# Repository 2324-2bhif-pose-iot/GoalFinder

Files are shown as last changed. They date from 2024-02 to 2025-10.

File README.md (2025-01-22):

# Goal Finder

IoT project in scope of POSE-PRPR and WLC, HTL Leonding, 2BHIF, JG 2324 in cooperation with Universität Wien.

[Erste Schritte](docs/gettting_started_de.md)

## Introduction

When visually impaired people play basket ball, they need acoustic assistance for locating the basket and as feedback if the basket is hit.

For locating the basket, a constant beeping is sufficient. For a hit, a triumph fanfare may be played. Miss detection may result in an according tune.

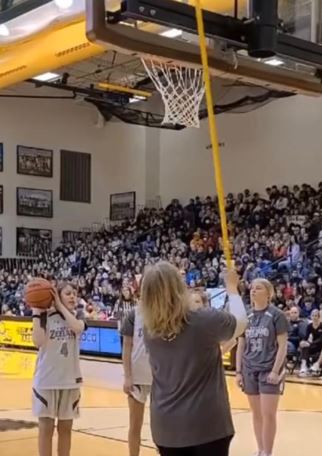
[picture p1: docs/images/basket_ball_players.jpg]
Basketball


Such assistance device may be directly mounted on the basket rack. They shall be easily mountable, e.g. by sliding them on the board or basket.

For hit detection, a short range laser distance sensor (ToF - time of flight sensor) is used. It is looking through the mesh of the basket and is therefore capable detecting a ball falling through the basket.

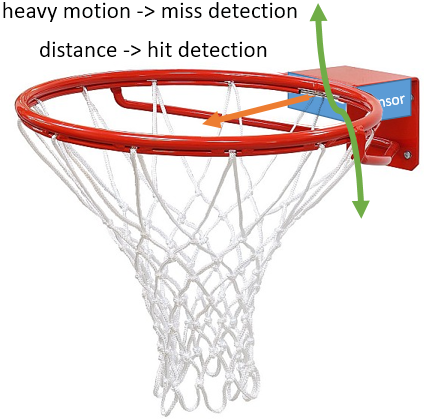
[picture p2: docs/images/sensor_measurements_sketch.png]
Sensor Sketch


Optionally, hitting the basket-board may be detected using an acceleration sensor. When a ball hits the board or the ring, heavy motion can be expected and detected. If the ball does not pass the basket in time, a miss is detected.

The sensor device shall be controlled via a web application designed for mobile devices, to operate the system on the (basketball) field. The application may also assist in the game, for instance by automatically counting hits for multiple players.

## Project Goals

A basketball assistance device as described about shall be developed and deployed in the field.

## Hardware Platform

+ SoC: ESP32, see [Random Nerd Tutorials: ESP32- Pinout](https://randomnerdtutorials.com/esp32-pinout-reference-gpios/)
+ Distance Sensor: ToF sensor connected via I²C, such as VL53L0X. see [YouTube: ToF used with ESP32](https://www.youtube.com/watch?v=HeMlcCDYCEk).
+ Option: Acceleration sensor (TBD).
+ Audio: ESP32 DAC with external pre-amplifier, see [YouTube: ESP32 Audio: I2S & Built-In DACs Explained](https://www.youtube.com/watch?v=lgDu88Y411o)
+ Power supply: Grid via power adapter or power bank.

## Use Cases and User Stories

1. As a user, I want to control the device via web application on a smart phone as well as on a desktop PC.
1. As a player, I want the device to provide acoustic hints of the basket location.
1. As a player, I want the device to sound a triumph tune when the ball hits the basket.
1. As a player, it would be great to hear a sound when the ball hits the basket rack but not the basket.
1. As a user, I want to connect to the device via WiFi network that is spread by the device.
1. As a user, I want to integrate the device into my WiFi network easily.
1. As a user, I want that the device time is synchronized with the real time of my timezone.
1. As a user, I want to update the device software over the air.

## Tasks

This section describes the first task to be tackled on a high-level base.

1. Specify a roadmap / time table for the given tasks and user story implementation.
1. Develop a software design showing the major software components and their relations as well as required communication protocols.
1. Integrate a WiFi setup and configuration on the device.
1. Integrate a web server on the device.
1. Integrate an SNTP client on the device, including SNTP configuration via integrated web server.
1. Implement the SW-component to measure distances via distance senor.
1. Option: Implement SW-component to measure motion via motion sensor.
1. Implement hit / miss detection based on the measured values.
1. Implement audio output
1. Integrate suitable audio tracks for signalling events.
1. Option: Implement audio feedback via Bluetooth.
1. Implement a web front-end suitable for configuring the sensor device
1. Implement a web front-end for game play.
1. Integrate and enable SWUOTA (software update over the air).

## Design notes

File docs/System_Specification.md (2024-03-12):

# System Specification

Hardware: 
- ESP32
- Distance Sensor
- Optional: Acceleration Sensor
- Audio ESP32
- Power Supply (power bank or power adapter)
  
Software:
- WiFi Client and WLAN integration
- Web Server
- SNTP Client
- Distance Sensor Software
- Optional: Motion Sensor Software
- Hit / Miss Detection
- Audio output, tracks, feedback (Audio manager)
- Web Application
- SWUOTA

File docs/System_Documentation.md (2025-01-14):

# Goalfinder System Documentation

## Summary

The Goalfinder is a device for visually impaired people, that need assistence locating the basket when playing basketball. This is done by a constant sound being played so that they can locate the basket. When a goal is scored a user specificated fanfare is played.

## Pin Configuration

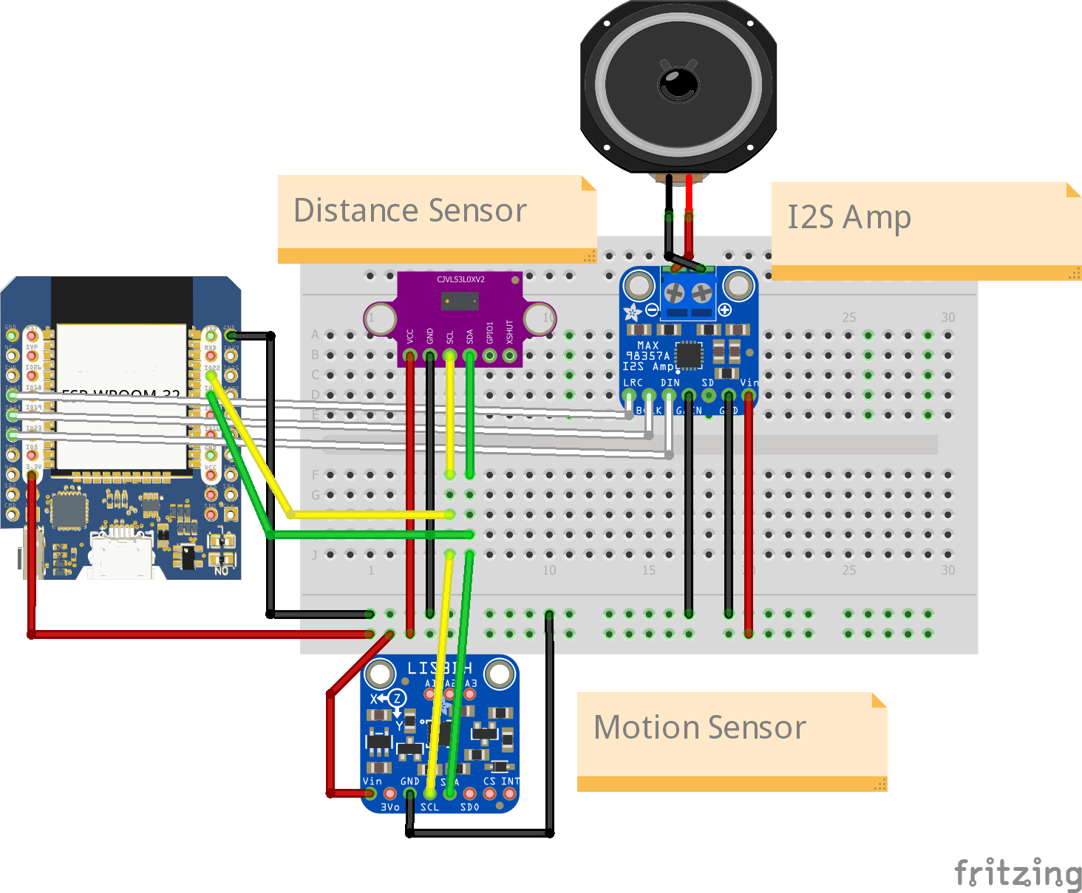
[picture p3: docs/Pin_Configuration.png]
Pins


### Components

- Distance Sensor
- Motion Sensor
- I2S Amp
- ESP 32

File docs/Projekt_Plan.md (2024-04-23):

# Projektplan

## Mitglieder
- Alex (A)
- Omar (O)
- Edin (E)
- Rabbi (R)

## Aufteilung
| Projektteil | Wer | Beginn    |
|-------------|-----|-------------|
| WLAN (HW)   | Alex |
| Web App | Alle |
| Web Server / SNTP Client (HW) | Alex / Omar
| Audio | Alex, Edin |
| Bluetooth Audio | Rabbi |
| ToF Sensor | Omar |
| Vibration Sensor | Rabbi |
| SWUOTA | Edin
| Optionale Sachen und Optimierung | Alle | Ende |

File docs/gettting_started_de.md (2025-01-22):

# Erste Schritte - Anleitung

## Inhaltsverzeichnis
- [Manuelles Flashen](#manuelles-flashen)
   - [Voraussetzungen (Tools)](#voraussetzungen-tools)
   - [Flashen des Systems](#flashen-des-systems)

- [Update über Webapp](#update-über-webapp)

Wenn der GoalFinder noch nicht aufgesetzt wurde oder der Flash-Speicher zurückgesetzt wurde, muss man die Firmware und das Filesystem manuell auf den GoalFinder flashen. Ansonsten kann man die neuste Firmware und das neuste Filesystem auf den GoalFinder über die Webapp laden.

## Manuelles Flashen

### Voraussetzungen (Tools)
- [CP210x Universal Windows Driver](https://www.silabs.com/developer-tools/usb-to-uart-bridge-vcp-drivers?tab=downloads)
- [Python](https://www.python.org/downloads/)

#### Installieren des Treibers
1. Entpacken Sie die Datei `CP210x_Universal_Windows_Driver.zip`
2. Öffnen Sie den entpackten Ordner
3. Drücken Sie mit der rechten Maustaste auf die Datei `silabser.inf` und wählen Sie `Installieren` aus
4. Folgen Sie den Anweisungen auf dem Bildschirm
5. Nun ist der erforderliche Treiber installiert

#### Installieren von Python und esptool.py
1. Installieren Sie die neuste Version von [Python](https://www.python.org/downloads/)
2. Führen Sie den Installer aus und folgen Sie den Anweisungen auf dem Bildschirm
3. Nun sollte Python installiert sein
4. Öffnen Sie die Eingabeaufforderung und führen Sie folgenden Befehl aus um `esptool.py` zu installieren.
   ``` 
   pip install esptool
   ```

### Flashen des Systems
1. Bauen Sie den GoalFinder auseinander um zum Micro-USB des ESP32 zu gelangen
2. Verbinden Sie den GoalFinder mithilfe eines Micro-USB Kabels mit dem Computer
3. Laden Sie die neusten `system.bin` und `littlefs.bin` Dateien von [Releases](https://github.com/2324-2bhif-pose-iot/GoalFinder/releases/latest) runter
4. Öffnen Sie die Eingabeaufforderung und navigieren Sie zum Ordner mit den heruntergeladenen Dateien mithilfe von dem Befehl `cd C:\Pfad\zum\Ordner`
5. Führen Sie folgenden Befehl in der Eingabeaufforderung aus um die Firmware zu flashen:
   ```
   python -m esptool -b 921600 write_flash 0x0 system.bin
   ```
6. Führen Sie folgenden Befehl in der Eingabeaufforderung aus um das Filesystem zu flashen:
   ```
   python -m esptool -b 921600 write_flash 2686976 littlefs.bin
   ```
7. Nun ist der GoalFinder betriebsbereit. Nun kann der GoalFinder durch die Webapp aktualisiert werden.

## Update über Webapp
1. Laden Sie die neusten `firmware.bin` und `littlefs.bin` Dateien von [Releases](https://github.com/2324-2bhif-pose-iot/GoalFinder/releases/latest) runter
2. Schließen Sie den GoalFinder an eine Stromquelle an
3. Verbinden Sie sich mit dem WiFi-Netz des GoalFinders
4. Öffnen Sie ihren Browser und geben Sie in die Adressleiste `goalfinder.local` ein
5. Es sollte sich nun die Webapp des GoalFinders öffnen
6. Navigieren Sie zu `Einstellungen > System`
7. Unter dem Punkt `Software Aktualisierung` drücken Sie auf `Auf Aktualisierung prüfen`
8. Wählen Sie zuerst `Firmware` und wählen Sie die zuvor heruntergeladene Datei `firmware.bin` aus
9. Warten Sie bis der Updatevorgang abgeschlossen wurde
10. Nun wird der Vorgang für das Filesystem wiederholt. Dabei wird `Filesystem` und anschließend die Datei `littlefs.bin` ausgewählt
11. Nun sollte der GoalFinder auf dem neusten Stand sein

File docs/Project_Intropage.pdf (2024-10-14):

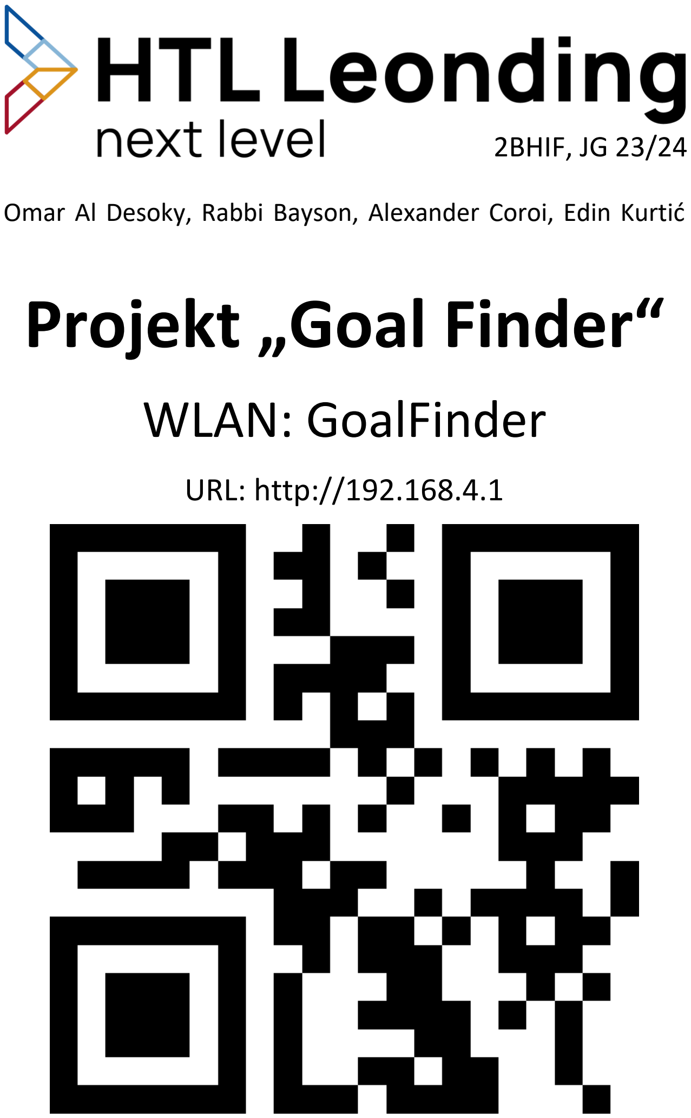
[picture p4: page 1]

Omar Al Desoky, Rabbi Bayson, Alexander Coroi, Edin Kurtić

# Projekt „Goal Finder“

# WLAN: GoalFinder

### URL: http://192.168.4.1

2BHIF, JG 23/24

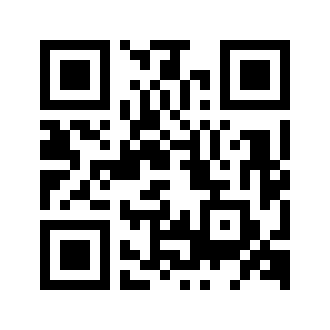
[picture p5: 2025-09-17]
docs/images/wifi_qr_goalfinder.png

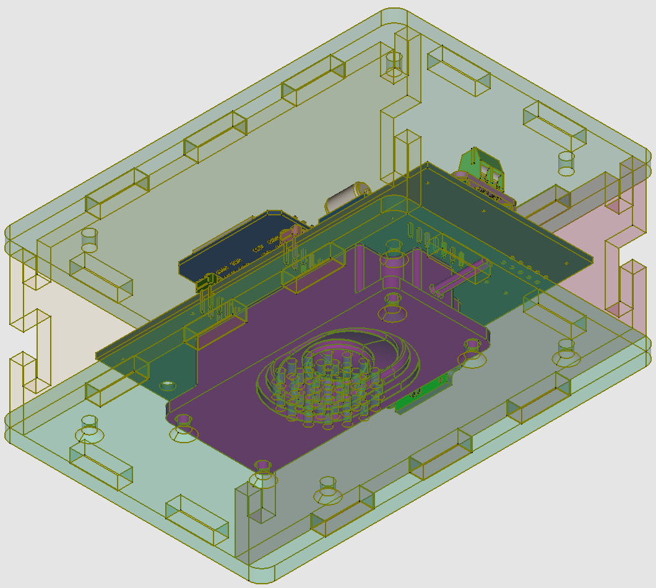
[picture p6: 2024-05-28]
docs/images/Goalfinder_r1.2_Case_r1.0_bottom.png

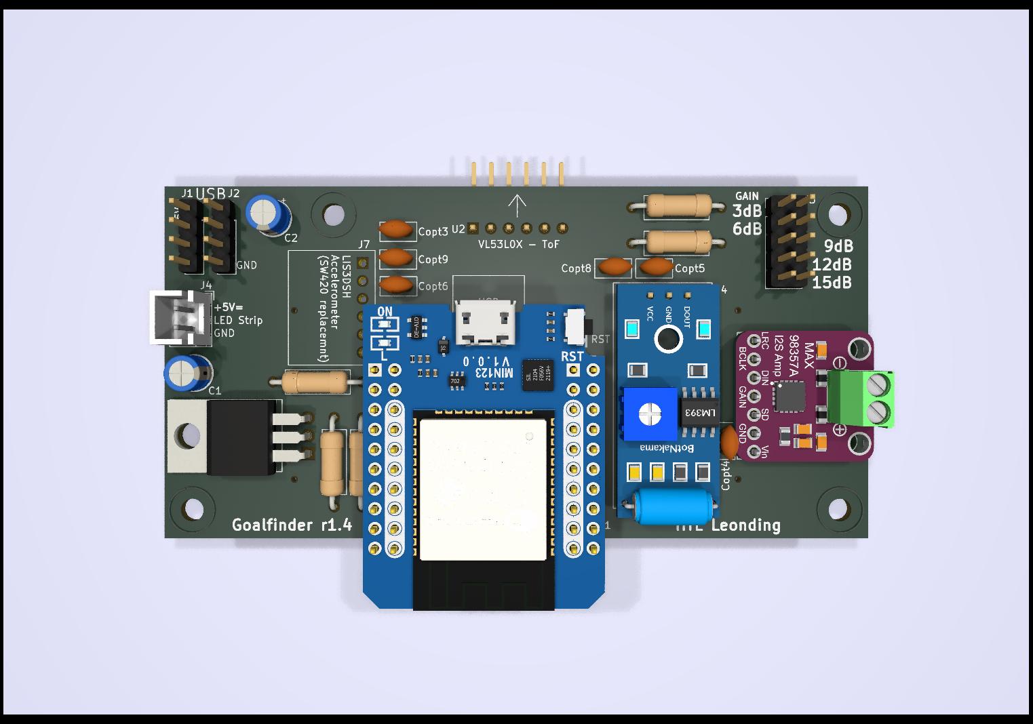
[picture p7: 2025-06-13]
docs/images/Goalfinder_PCB_r1.4_THT_Vibration_front.jpg

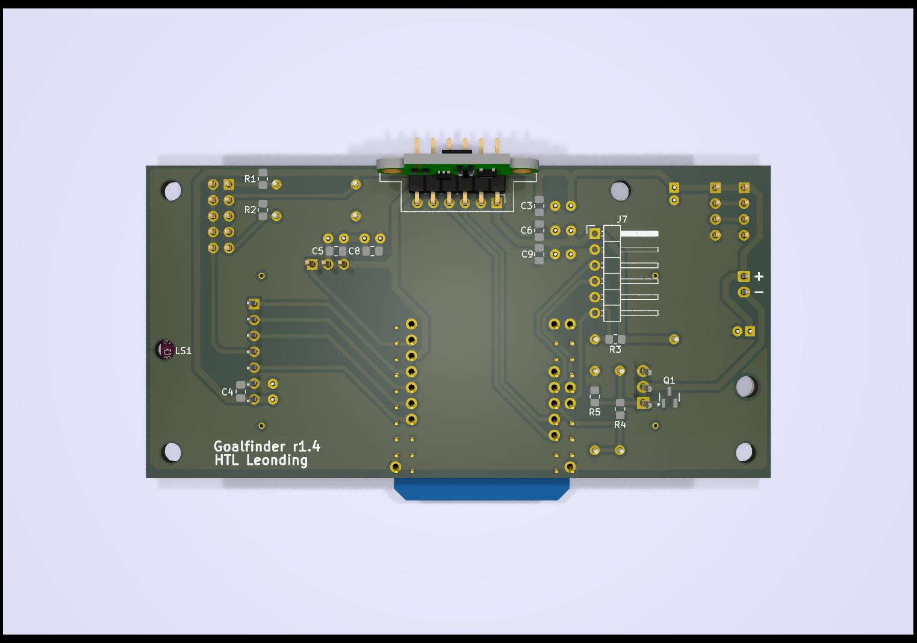
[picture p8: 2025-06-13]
docs/images/Goalfinder_PCB_r1.4_THT_Vibration_back.jpg

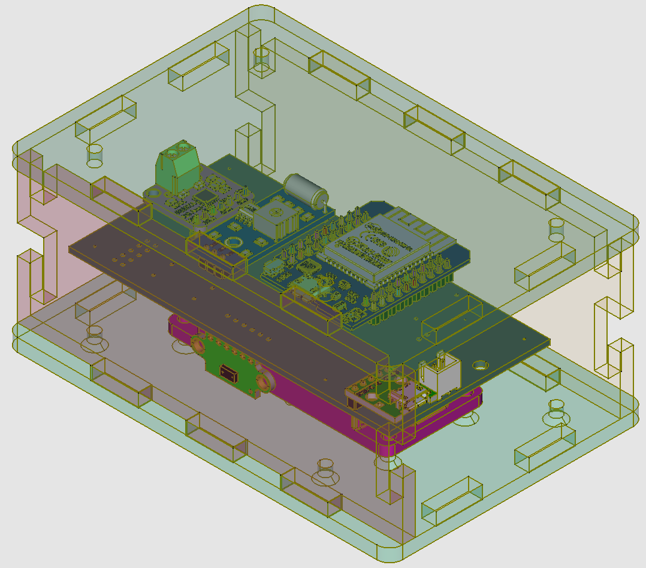
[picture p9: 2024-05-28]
docs/images/Goalfinder_r1.2_Case_r1.0_top.png

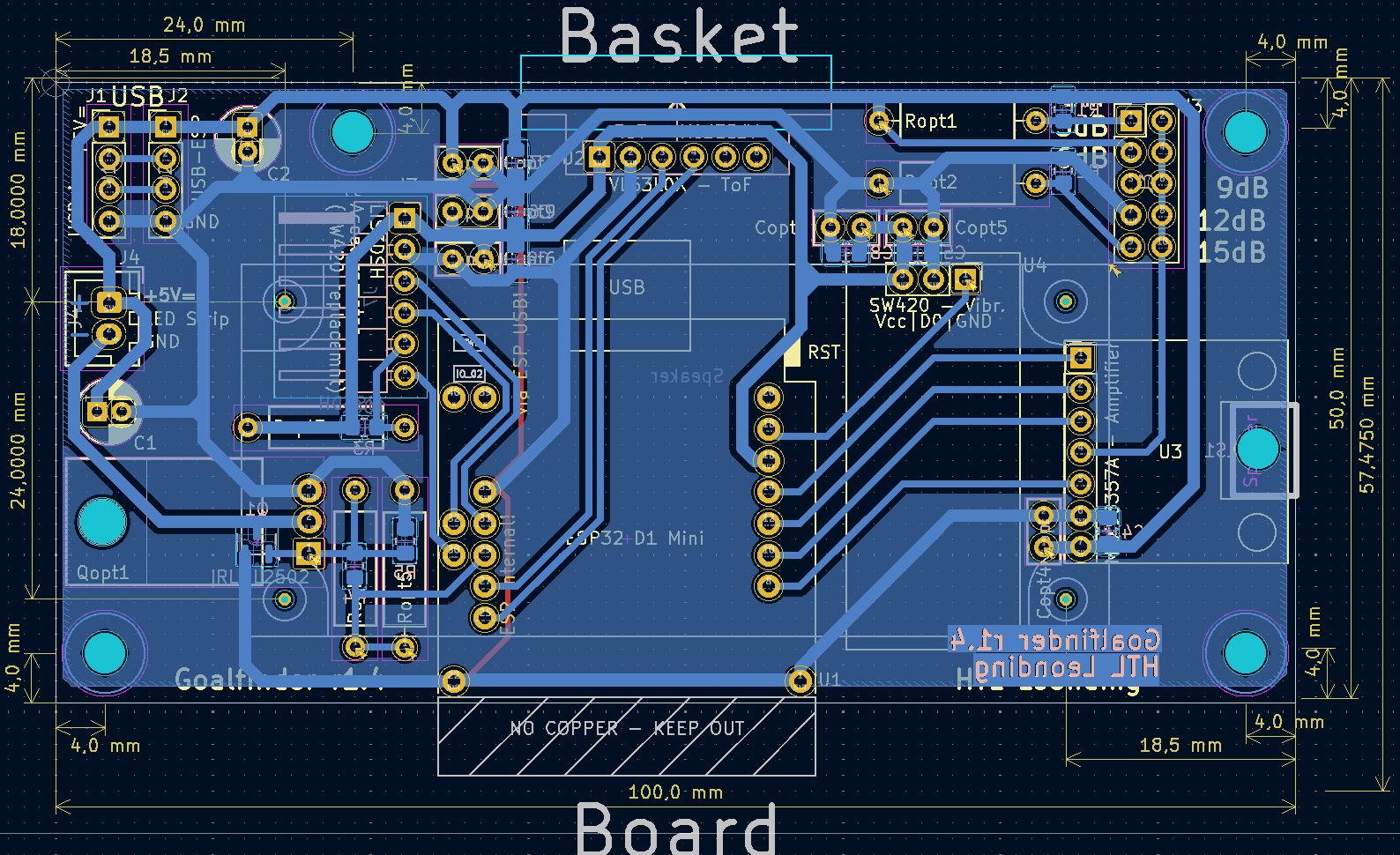
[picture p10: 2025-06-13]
docs/Goalfinder_PCB_r1.4_layout.png

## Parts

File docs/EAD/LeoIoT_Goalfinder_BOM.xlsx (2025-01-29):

Reference | Value | Footprint | Qty | Beschreibung | Comment / Supplier
C1 | 22µF | Capacitor_THT:CP_Radial_D5.0mm_P2.00mm | 1 | Polarized capacitor, small symbol
C2 | 4,7µF | Capacitor_THT:CP_Radial_D5.0mm_P2.00mm | 1 | Unpolarized capacitor, small symbol
C3 | 0,1µF | Capacitor_THT:C_Rect_L13.0mm_W4.0mm_P10.00mm_FKS3_FKP3_MKS4 | 1 | Unpolarized capacitor, small symbol
C4,C5,C6,C7,C8 | 100nF | Capacitor_SMD:C_0805_2012Metric_Pad1.18x1.45mm_HandSolder | 5 | Unpolarized capacitor, small symbol
Copt4,Copt5,Copt6,Copt7,Copt8 | 100nF | Capacitor_THT:C_Disc_D5.0mm_W2.5mm_P2.50mm | 0 | Unpolarized capacitor, small symbol | Optional for THT parts, replaces C4, C5, C6, C7, C8 https://www.reichelt.de/de/de/shop/produkt/keramik-kondensator_100_nf_-20_80_y5v_50_100_v_rm_5-9265
J2 | LED Strip | Connector_JST_2.54:JST_XH_B2B-XH-A_1x02_P2.54mm_Vertical | 1 | Connector for LED Strip
J1 | USB_B_Micro_Breakout | Breakout_Boards:Micro-USB_BreakoutBoard | 1 | USB Micro Type B connector | https://www.amazon.de/KARELLS-Steckerkabel-Verl%C3%A4ngerungskabel-Stromladekabel-Ersatzkabel/dp/B0D6362W88
D1, J1e1 | Conn_01x02_Pin | 5V LED Strip, max 30W | 1 | LED Strip with connector suitable for J2 | https://www.amazon.de/GOMING-COB-Selbstklebend-Wasserdicht-Lichtband/dp/B09VGR6PWH/ref=sr_1_4?th=1
J3 | GAIN | Connector_PinHeader_2.54mm:PinHeader_2x05_P2.54mm_Vertical | 1 | Jumper bar for gain selection | either wire bridge or:
 |  |  |  |  | Jumper: https://www.reichelt.de/de/de/shop/produkt/kurzschlussbruecke_schw_m_grifflasche-9019
 |  |  |  |  | Pin Header: https://www.reichelt.de/de/de/shop/produkt/stiftleiste_2x20-pol_vergoldet_2_54mm-235664
LS1 | Speaker | Breakout_Boards:Mono-Enclosed_Speaker_70x30x17mm_onboard | 1 | Speaker, 3 W, 8 Ohm | https://www.amazon.de/dp/B09PL6XFHC
Q1 | IRFZ44N | Package_TO_SOT_THT:TO-220-3_Horizontal_TabDown | 1 | FET | https://www.reichelt.de/de/de/shop/produkt/mosfet_n-ch_60v_48a_110w_0_023r_to220ab-257487
R1,R2 | 100k | Resistor_THT:R_Axial_DIN0309_L9.0mm_D3.2mm_P12.70mm_Horizontal | 2 | Resistor
R4 | 1k | Resistor_THT:R_Axial_DIN0309_L9.0mm_D3.2mm_P12.70mm_Horizontal | 1 | Resistor
R5 | 33k | Resistor_THT:R_Axial_DIN0309_L9.0mm_D3.2mm_P12.70mm_Horizontal | 1 | Resistor
U1 | ESP32_D1_mini | ESP32_D1_mini:ESP32_D1_mini | 1 | ESP32 D1 mini from AZ-Delivery | https://www.amazon.de/AZDelivery-Bluetooth-Internet-Entwicklungsboard-kompatibel/dp/B08BTYCGVV
U2 | VL53L0X_Breakout | Breakout_Boards:VL53L0X_Breakout_Board_vertical_flat | 1 | 2m distance ranging ToF sensor, Optical LGA12 | https://www.amazon.de/AZDelivery-VL53L0X-Flight-kompatibel-Arduino/dp/B086TSNTFD
U3 | MAX98357A_Breakout | Breakout_Boards:MAX98357A_Breakout_Board | 1 | Mono DAC with amplifier, I2S, PCM, TDM, 32-bit, 96khz, 3.2W, TQFP-16 | https://www.amazon.de/AZDelivery-filterloses-Breakout-Modul-Decoder-Modul-Anwendungsbereich/dp/B09PL947ZG
U4 | SW420_Breakout | Breakout_Boards:SW420_Breakout_Board_Horizontal | 1 | Vibrationsensor, Shocksensor | https://www.amazon.de/AZDelivery-Vibration-Sch%C3%BCttel-Ersch%C3%BCtterung-Arduino/dp/B07V9CZ89G

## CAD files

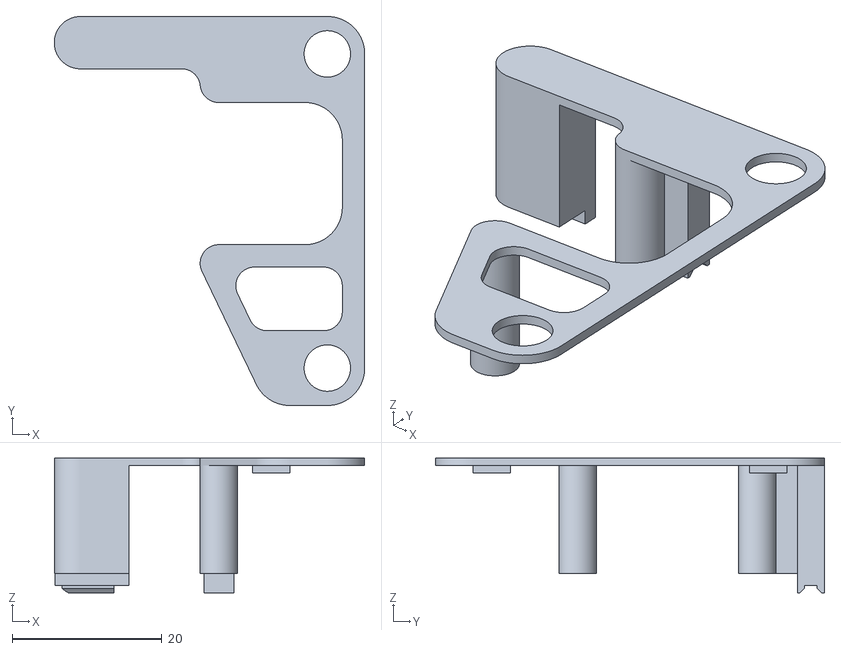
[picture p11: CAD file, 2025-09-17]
docs/Housing/LeoIoT-Goalfinder_r1.4_cpct_Bracket_Top-Right.stl
41.5 x 52.0 x 18.0

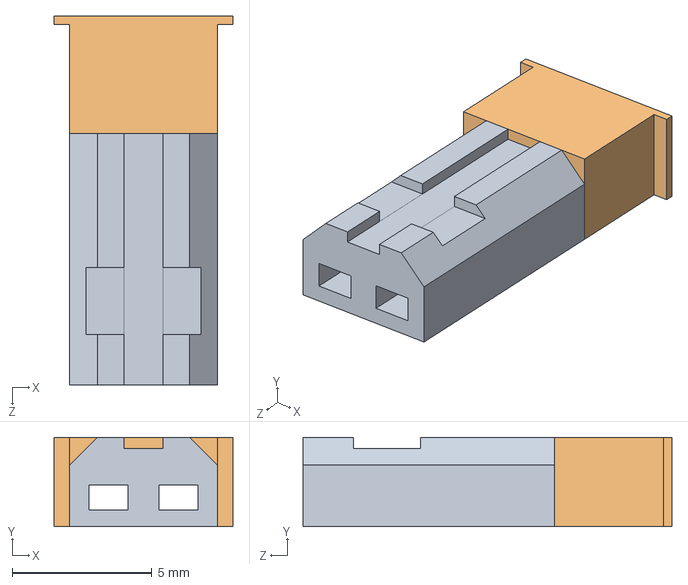
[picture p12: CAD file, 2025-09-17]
docs/Housing/JST-SYP_Female.step
6.40 x 3.20 x 13.2 mm

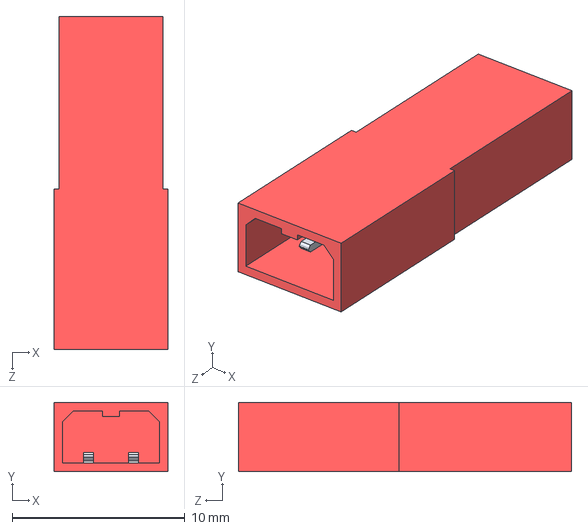
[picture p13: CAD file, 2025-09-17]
docs/Housing/JST-SYP_Male.step
6.60 x 4.00 x 19.3 mm

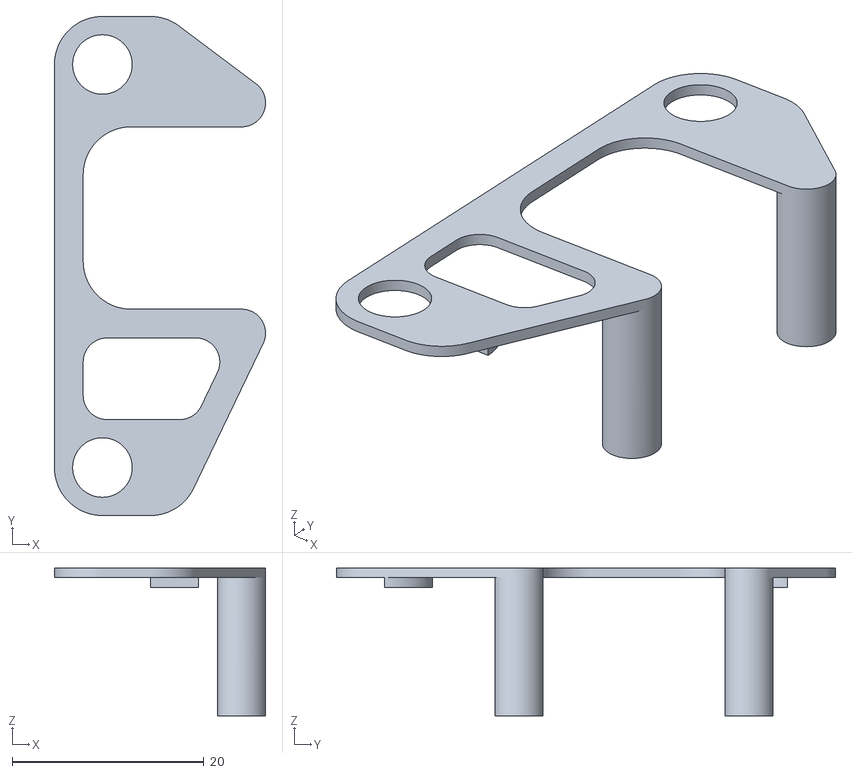
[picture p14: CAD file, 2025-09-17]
docs/Housing/LeoIoT-Goalfinder_r1.4_cpct_Bracket_Top-Left.stl
22.0 x 52.0 x 15.4

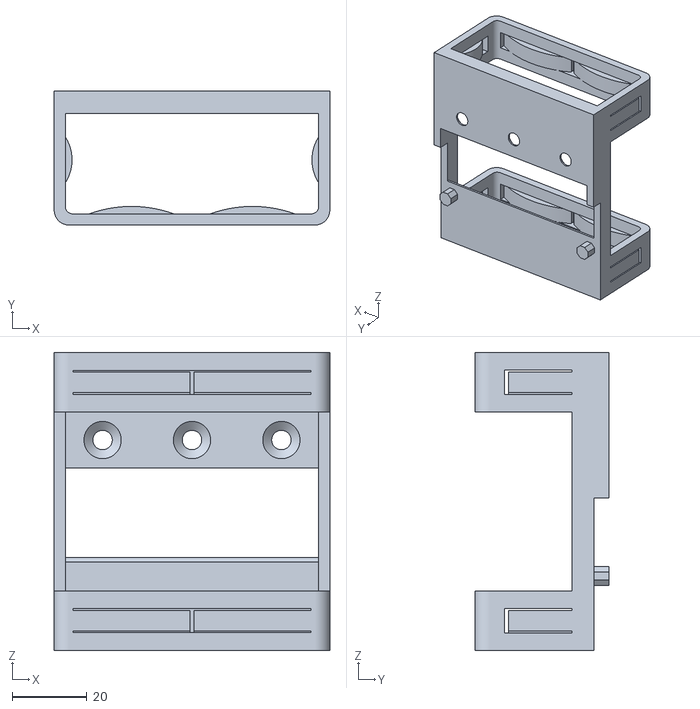
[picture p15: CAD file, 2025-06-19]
docs/Housing/Powerbank-Holder_Anker.stl
74.0 x 36.0 x 80.0

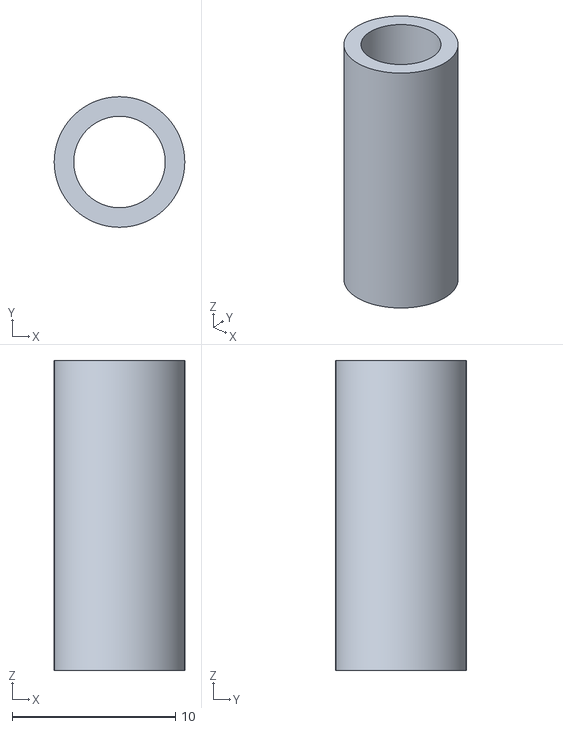
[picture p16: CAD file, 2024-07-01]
docs/Housing/Distance-19.stl
8.00 x 8.00 x 19.0

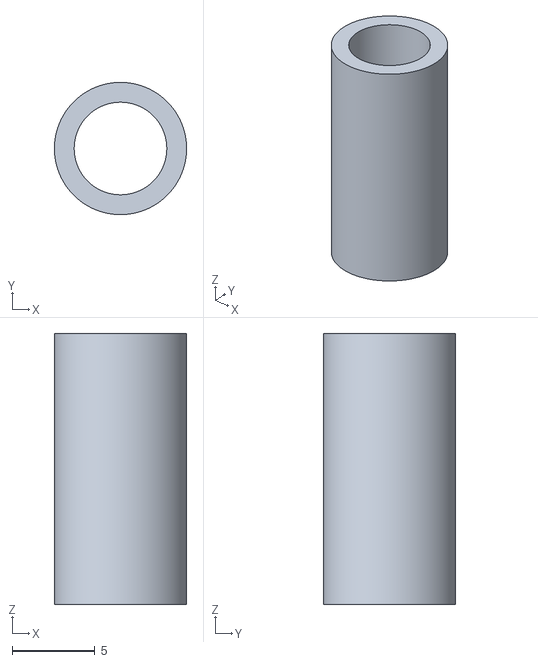
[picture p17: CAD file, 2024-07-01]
docs/Housing/Distance-16.4.stl
8.00 x 8.00 x 16.4

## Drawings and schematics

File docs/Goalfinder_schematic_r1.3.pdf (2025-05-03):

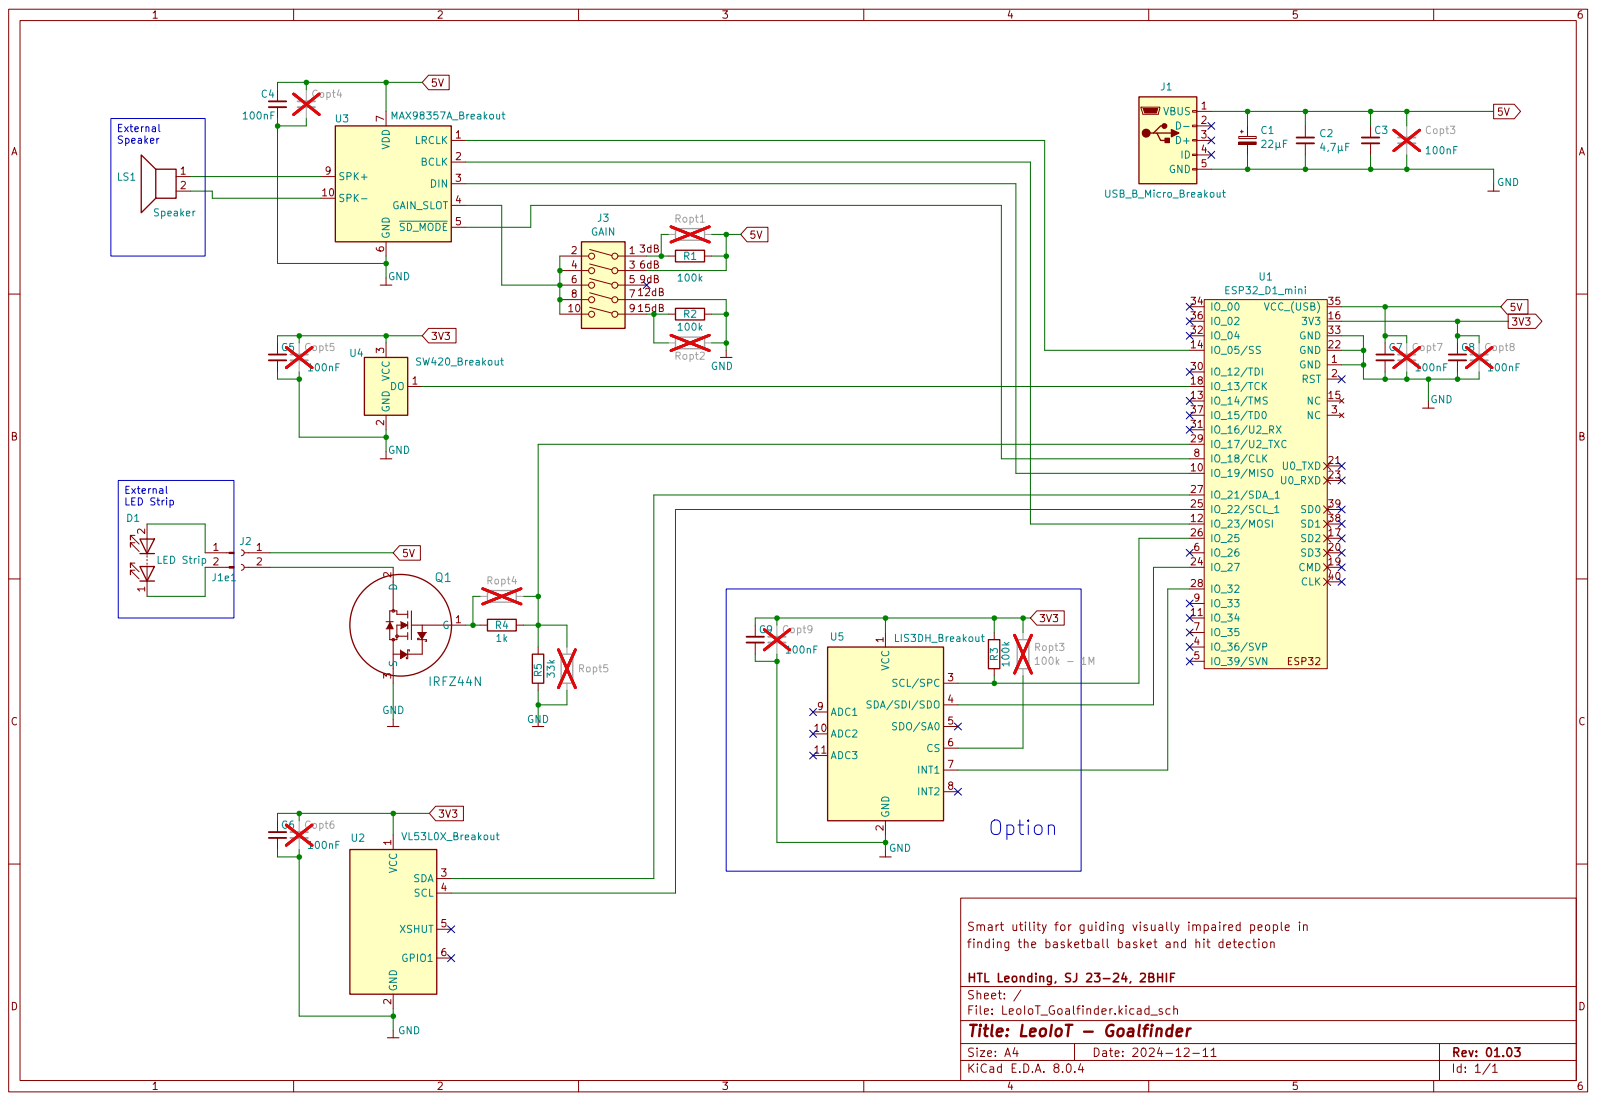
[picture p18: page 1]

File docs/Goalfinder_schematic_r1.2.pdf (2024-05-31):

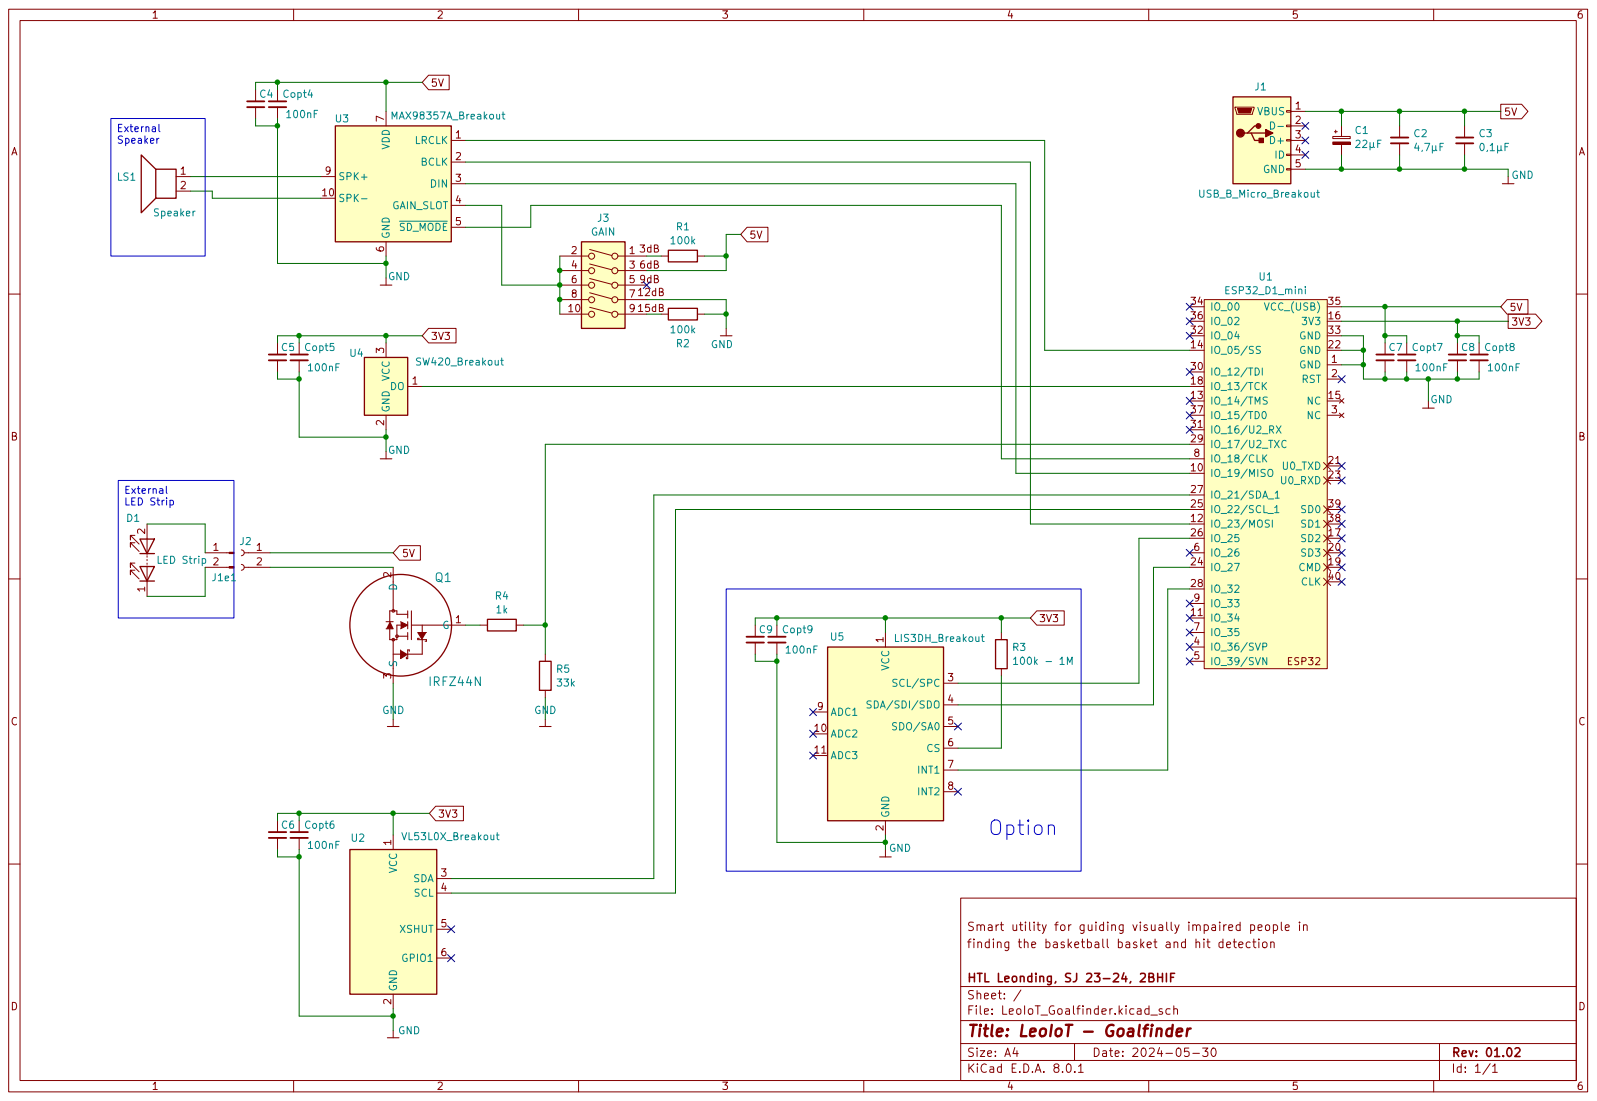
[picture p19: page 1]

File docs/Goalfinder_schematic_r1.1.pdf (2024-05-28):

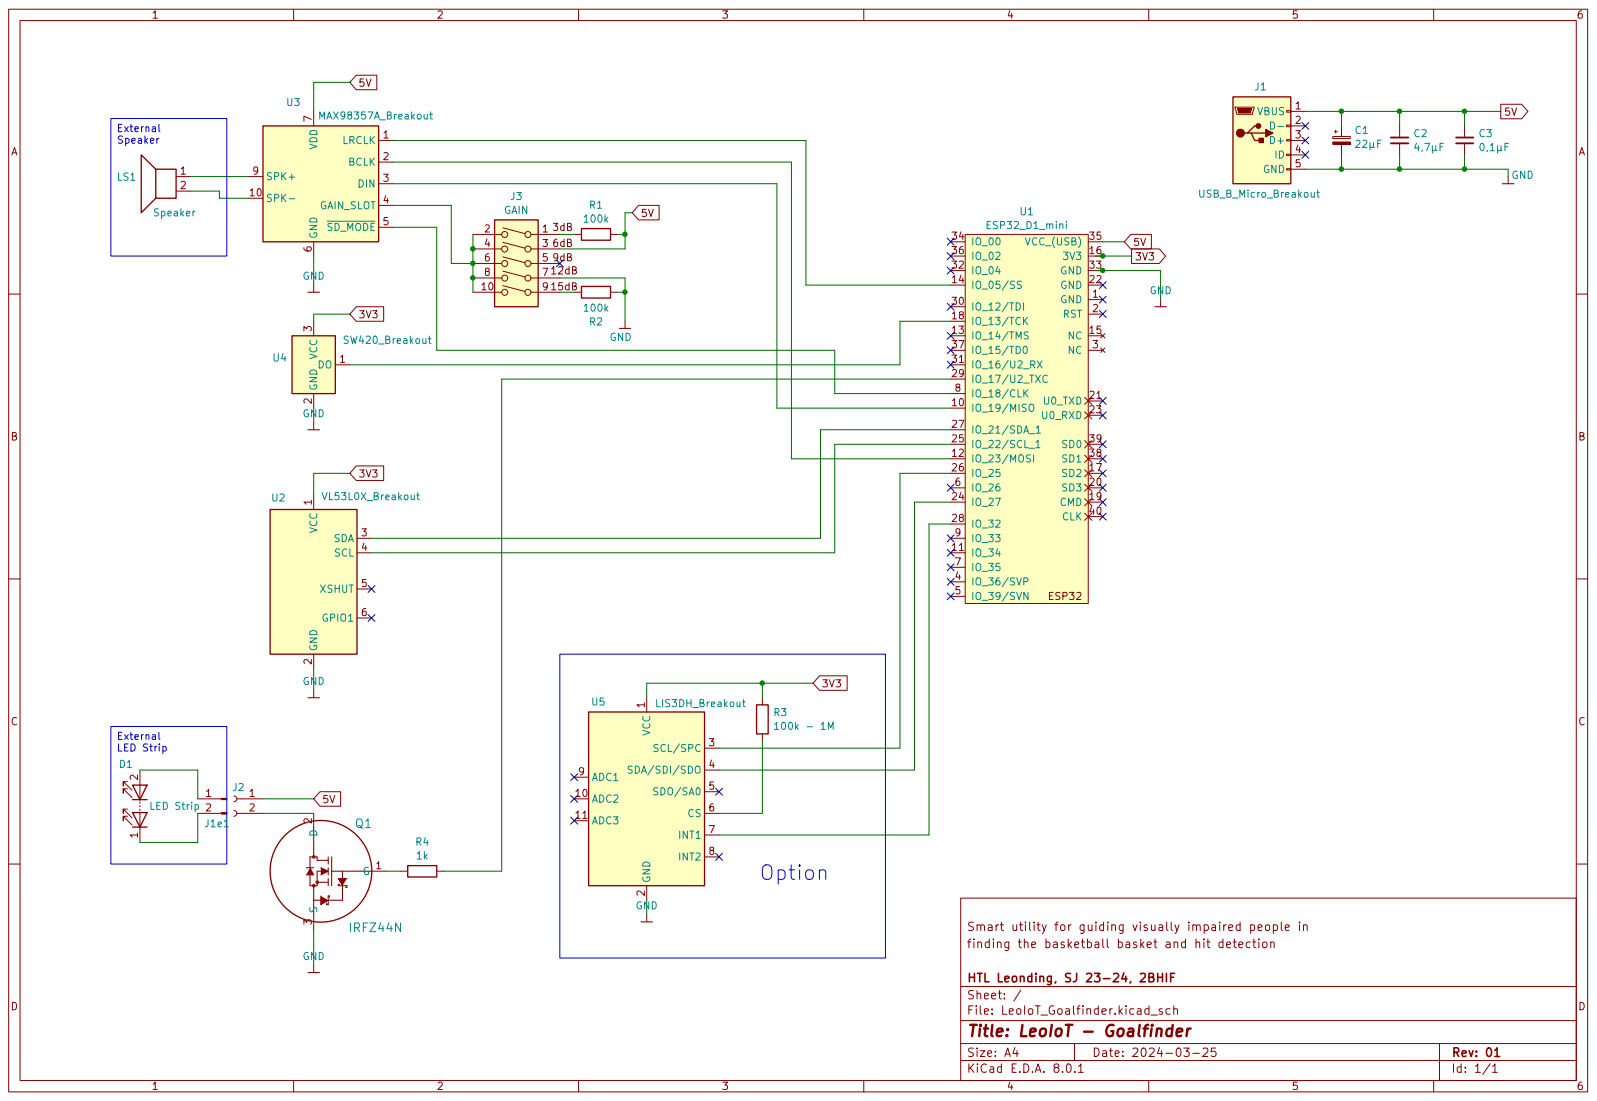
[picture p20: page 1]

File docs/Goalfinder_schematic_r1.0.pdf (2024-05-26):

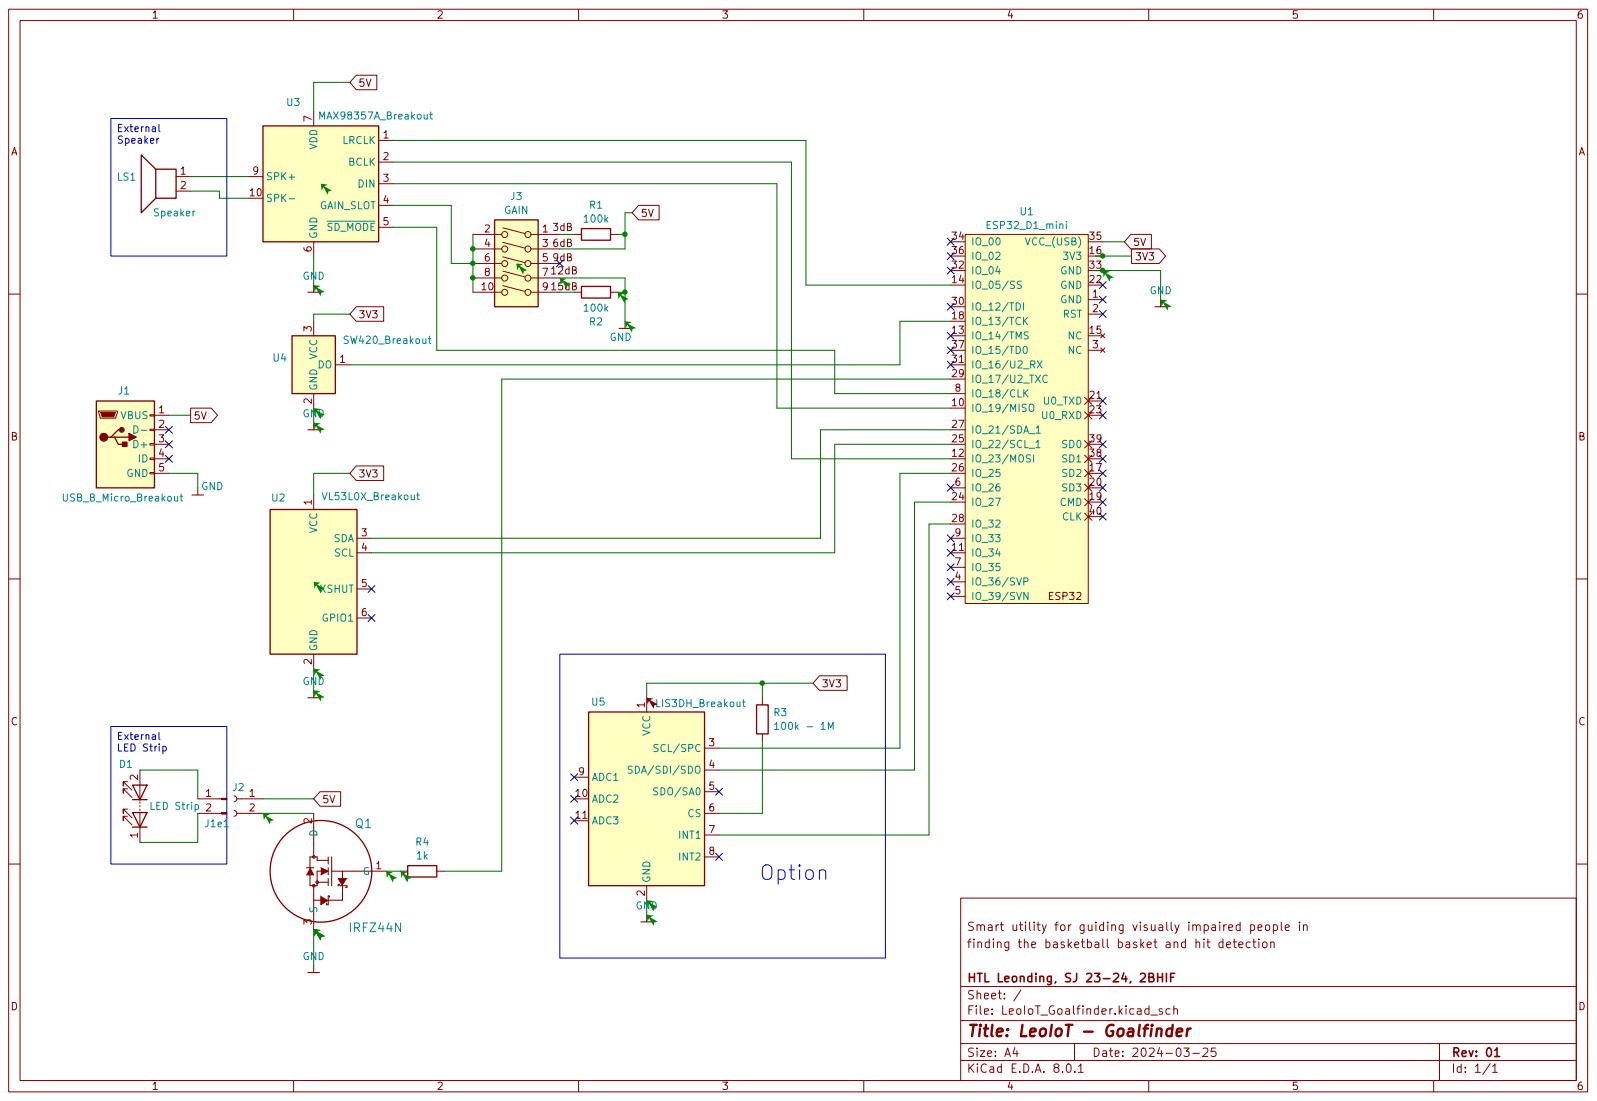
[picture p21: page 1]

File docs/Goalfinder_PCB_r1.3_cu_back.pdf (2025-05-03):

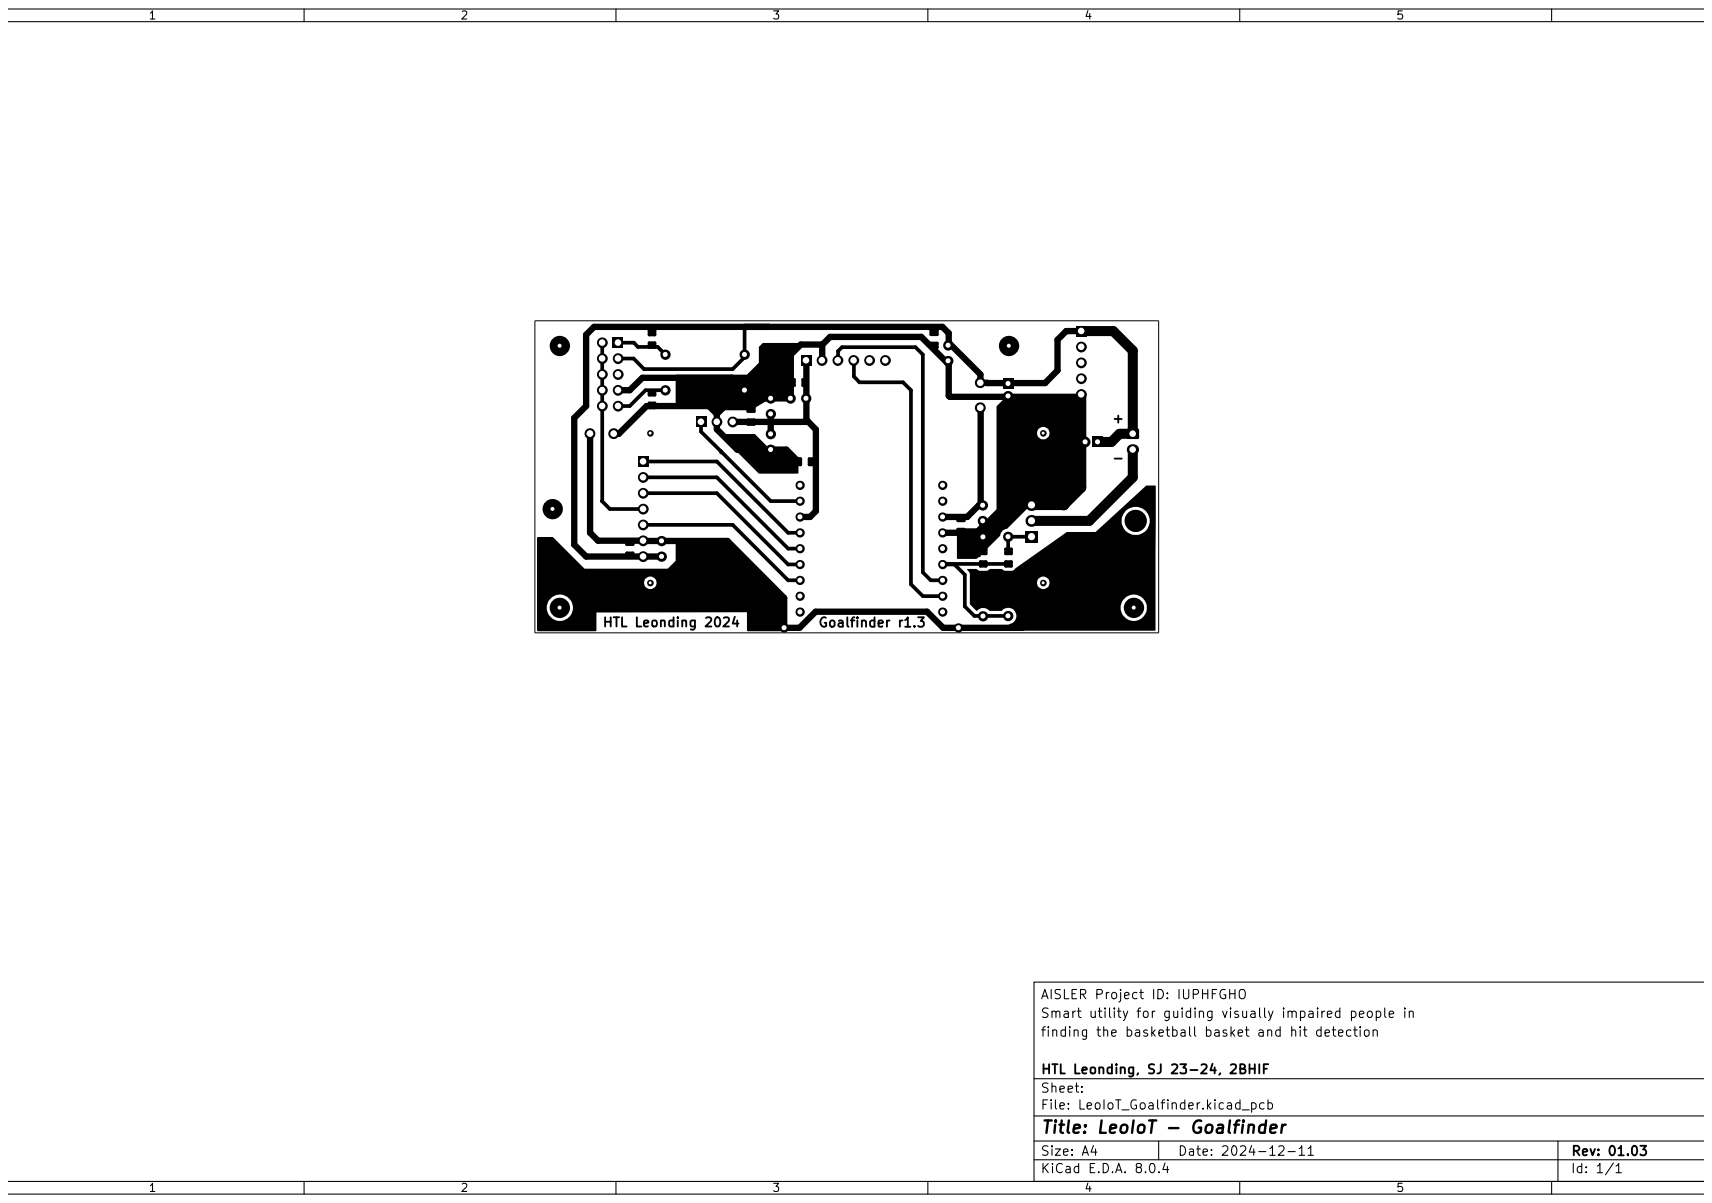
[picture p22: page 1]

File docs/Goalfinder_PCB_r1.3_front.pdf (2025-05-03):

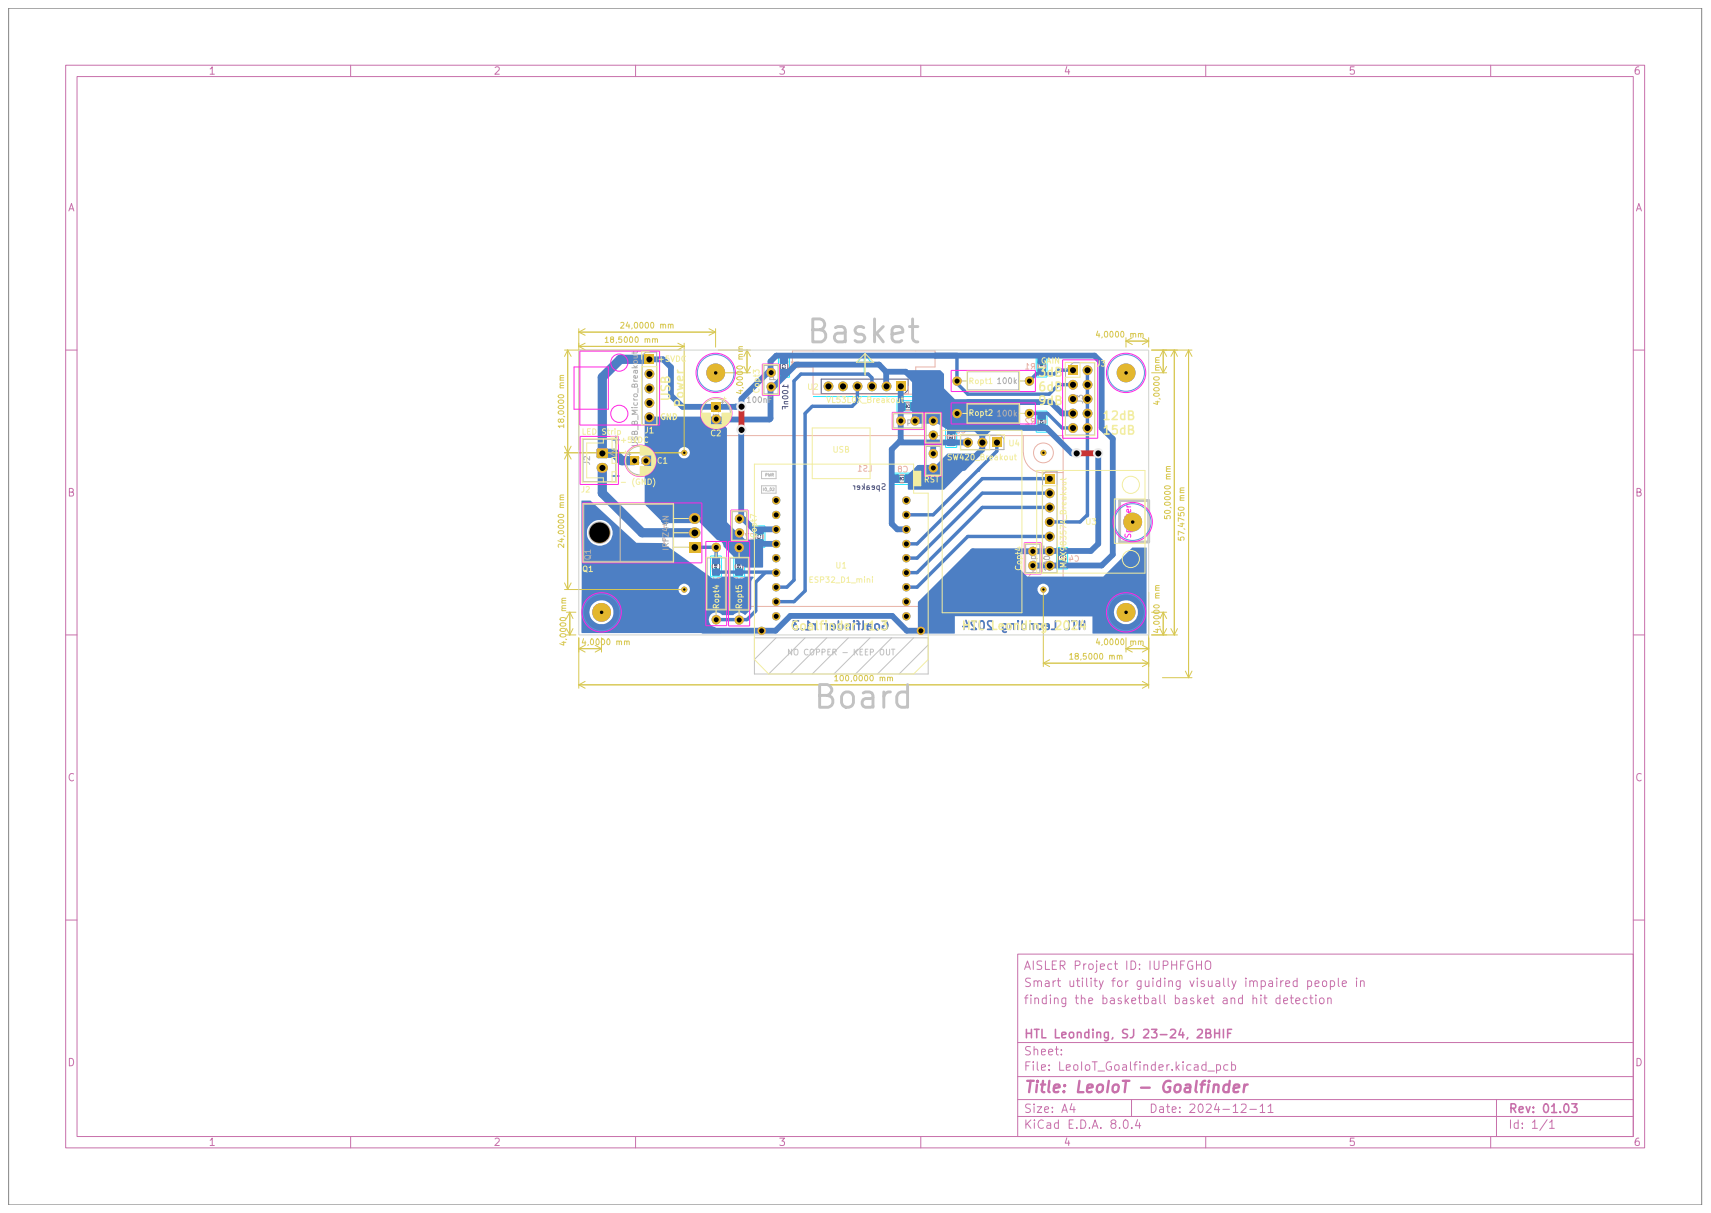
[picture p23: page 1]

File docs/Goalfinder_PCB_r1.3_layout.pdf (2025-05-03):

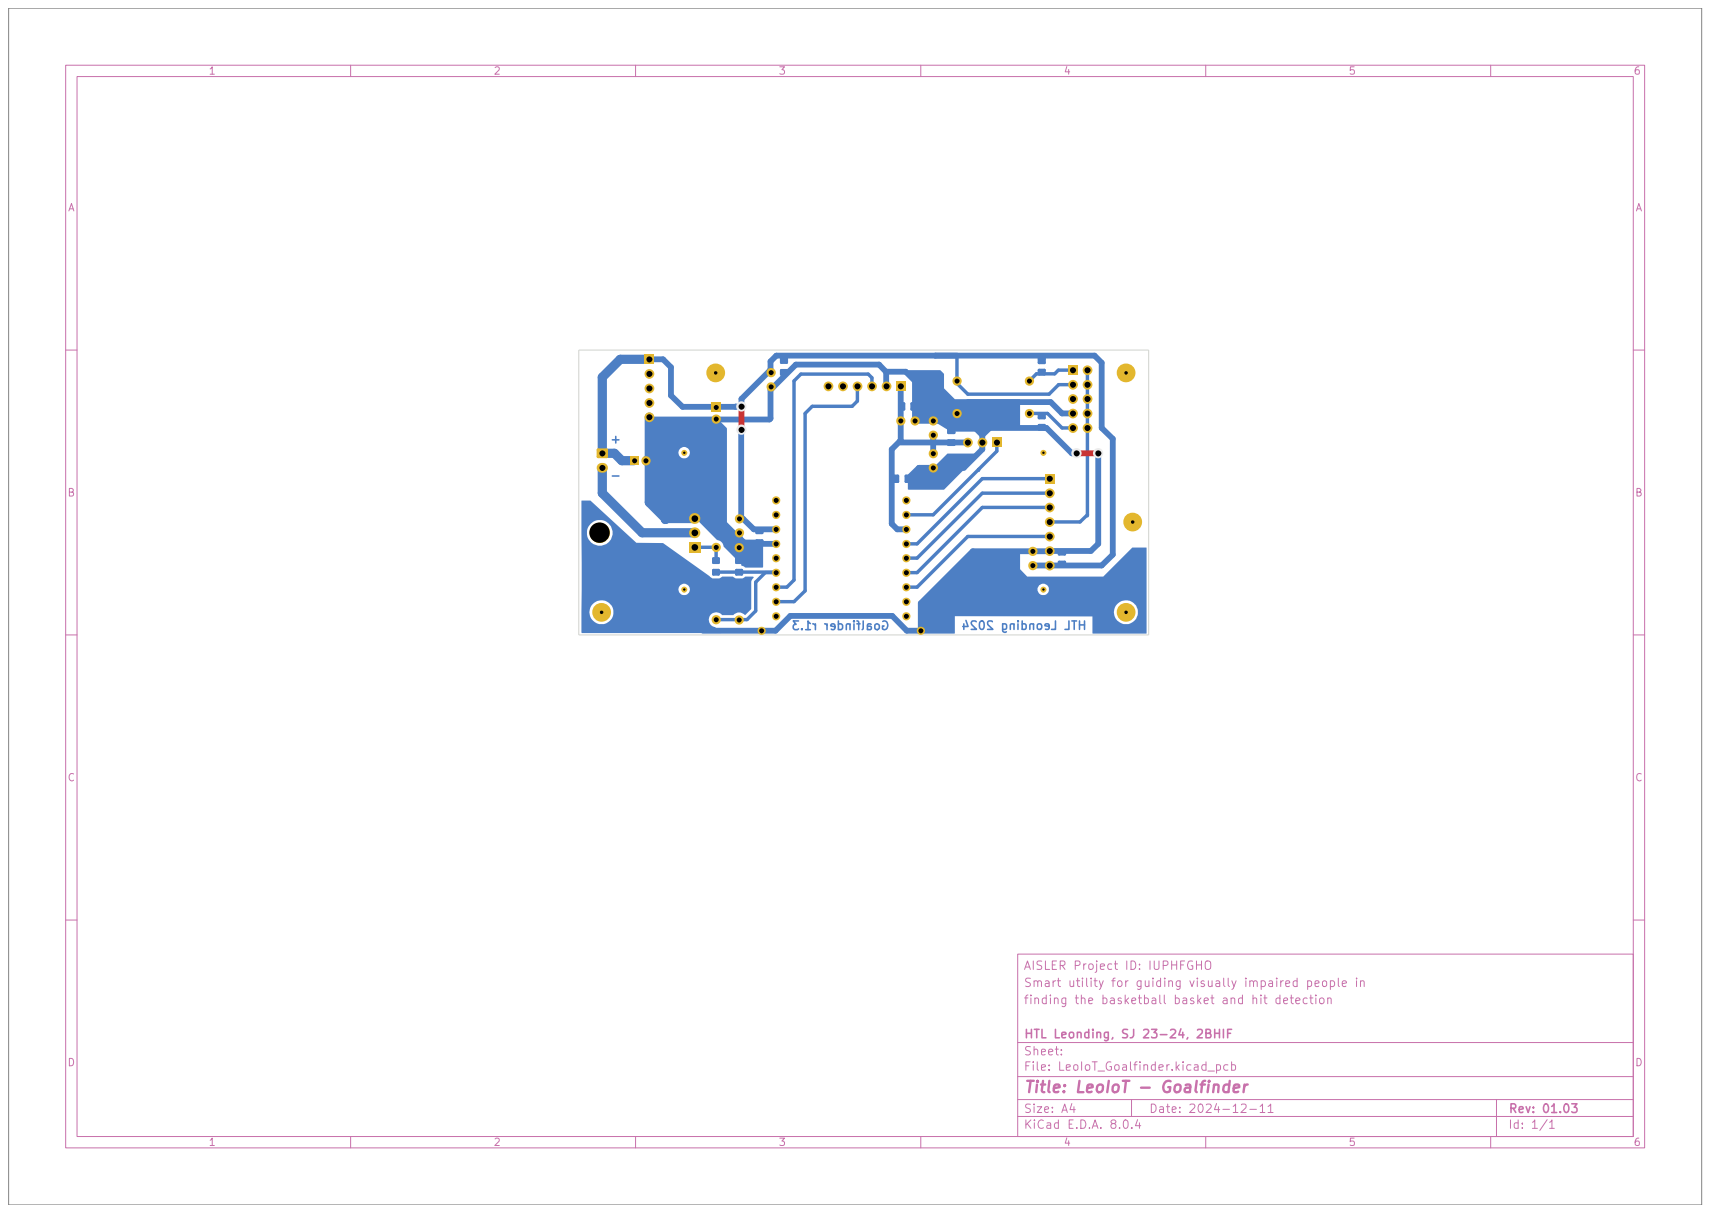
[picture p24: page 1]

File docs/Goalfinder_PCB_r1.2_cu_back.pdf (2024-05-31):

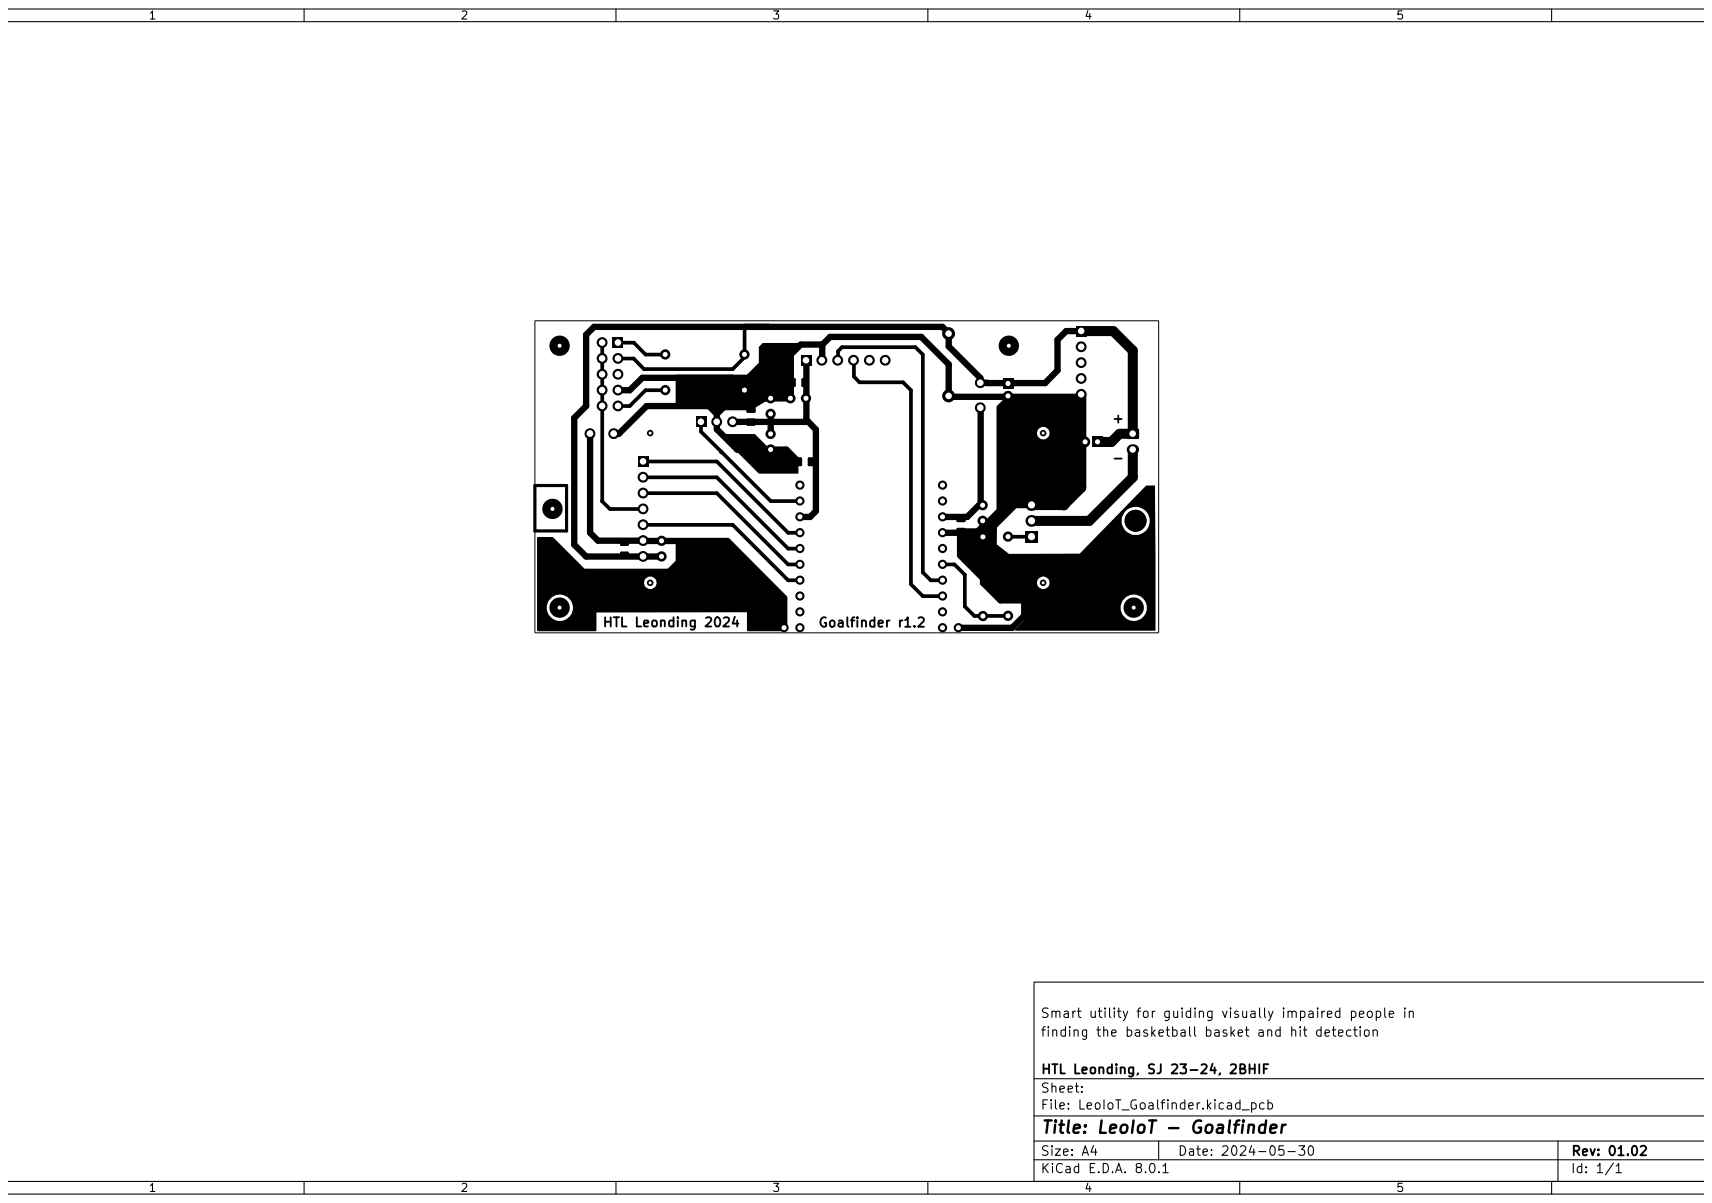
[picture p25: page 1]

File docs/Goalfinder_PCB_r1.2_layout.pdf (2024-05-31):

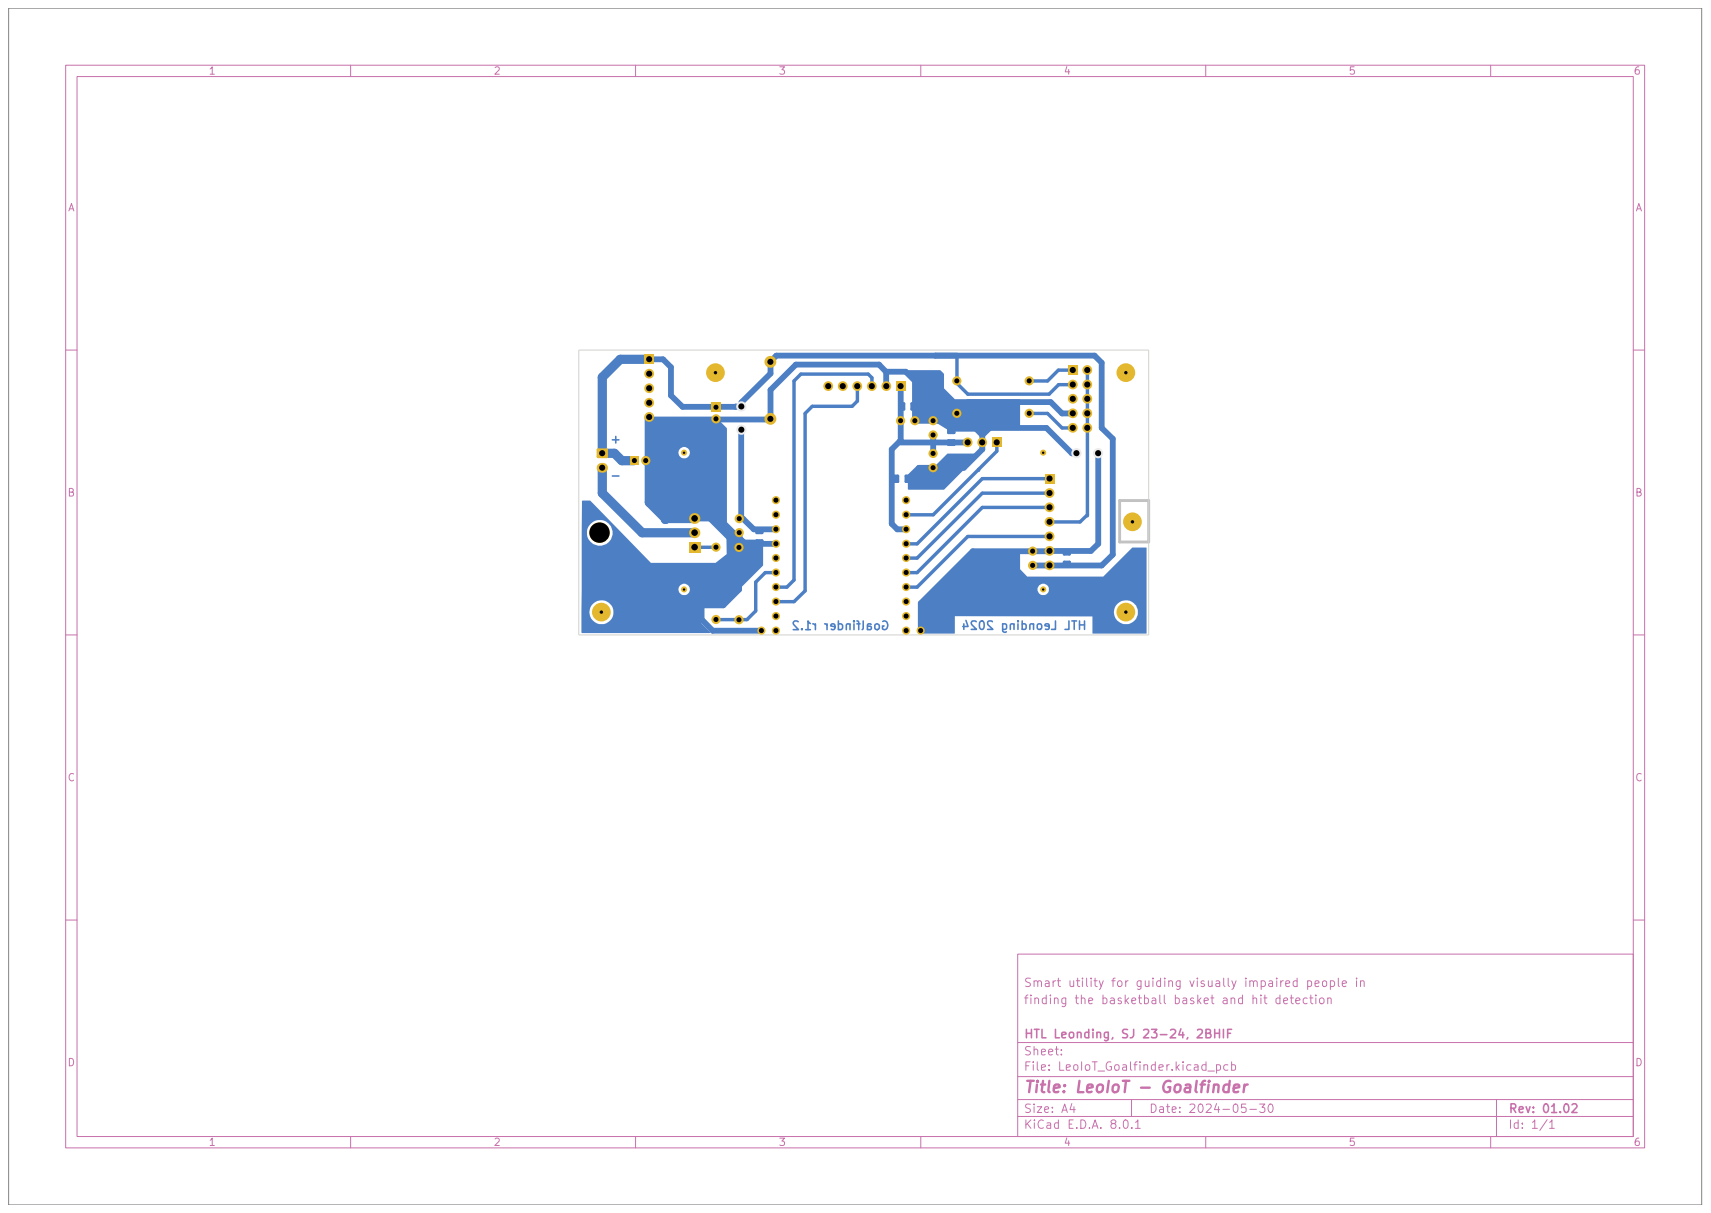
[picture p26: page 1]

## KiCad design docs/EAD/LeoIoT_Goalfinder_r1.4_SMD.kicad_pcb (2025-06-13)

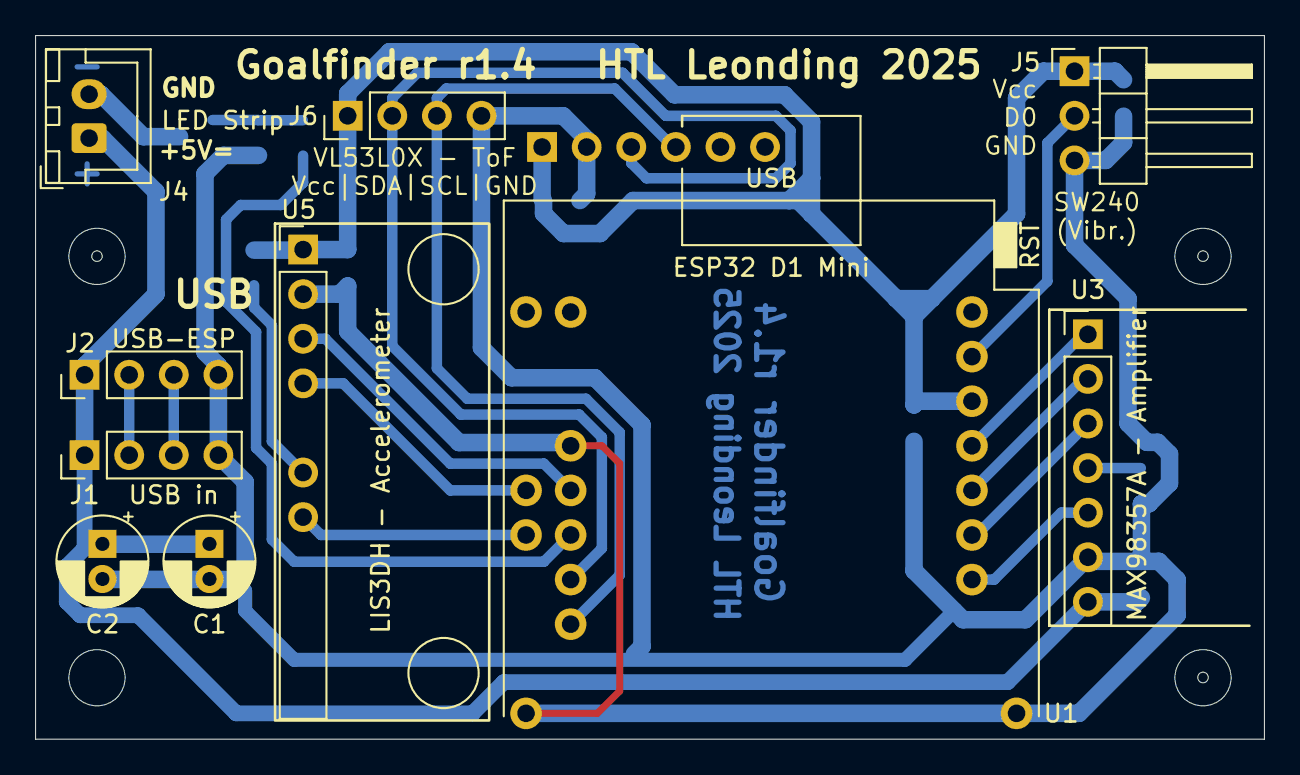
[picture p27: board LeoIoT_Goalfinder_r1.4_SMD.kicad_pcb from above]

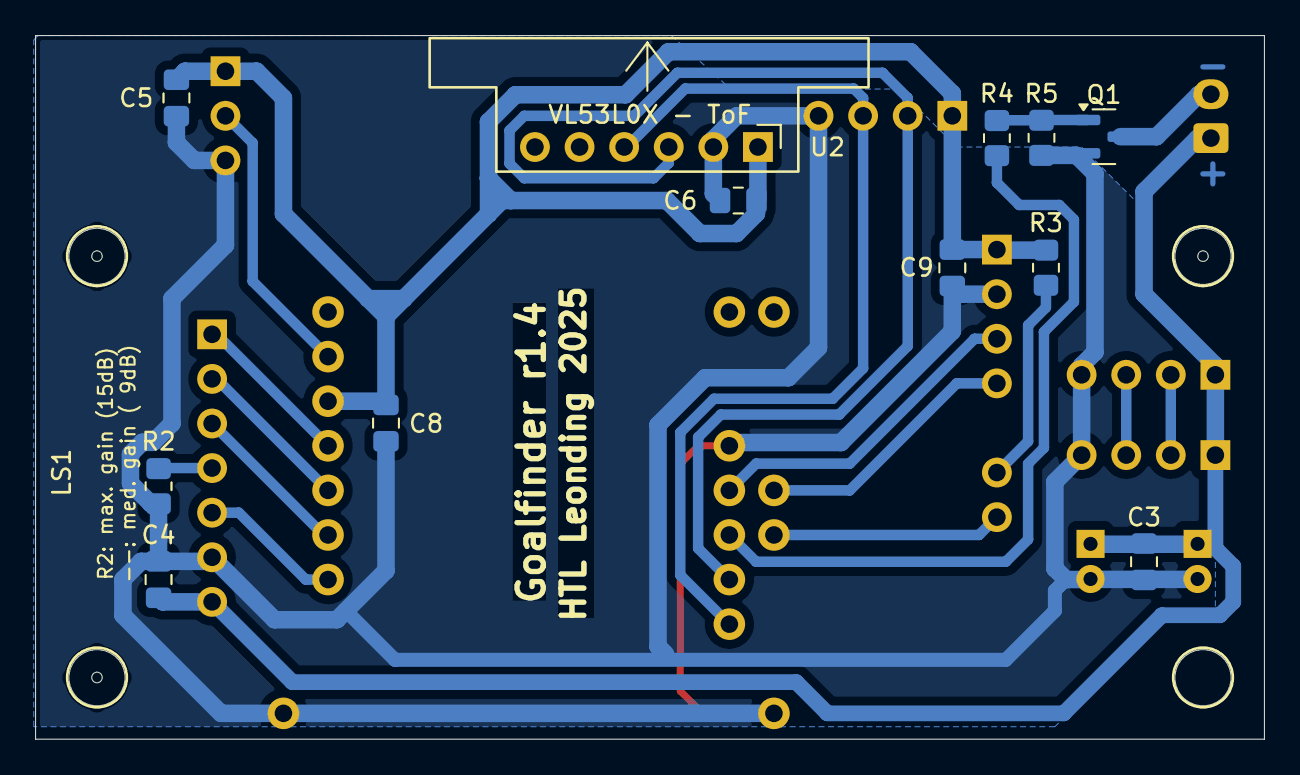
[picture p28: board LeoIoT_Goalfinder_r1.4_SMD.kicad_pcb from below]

Board: 2 copper layers, 70.0 x 40.1 mm, 27 parts (13 on the bottom side), 20 nets.

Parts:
C1: 22µF; CP_Radial_D5.0mm_P2.00mm
C2: 4,7µF; CP_Radial_D5.0mm_P2.00mm
C3, C4, C5, C6, C8, C9: 100nF; C_0805_2012Metric_Pad1.18x1.45mm_HandSolder
J1: USB in; PinHeader_1x04_P2.54mm_Vertical
J2: USB-ESP; PinHeader_1x04_P2.54mm_Vertical
J4: LED Strip; JST_XH_B2B-XH-A_1x02_P2.50mm_Vertical
J5: SW240 - Vcc/D0/GND; PinHeader_1x03_P2.54mm_Horizontal
J6: VL53L0X-ToF Vcc/SDA/SCL/GND; PinHeader_1x04_P2.54mm_Vertical
LS1: Speaker; Mono-Enclosed_Speaker_70x30x17mm_onboard
MH1, MH2, MH3, MH4: MountingHole_3.2mm_M3
Q1: IRLML2502; SOT-23
R2, R3: 100k; R_0805_2012Metric_Pad1.20x1.40mm_HandSolder
R4: 1k; R_0805_2012Metric_Pad1.20x1.40mm_HandSolder
R5: 33k; R_0805_2012Metric_Pad1.20x1.40mm_HandSolder
U1: ESP32 D1 Mini; ESP32_D1_mini
U2: VL53L0X - ToF; VL53L0X_Breakout_Board_vertical_flat
U3: MAX98357A - Amplifier; MAX98357A_Breakout_Board
U5: LIS3DH - Accelerometer; LIS3DH_Breakout_Board

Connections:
3V3: C5.1, C6.1, C8.1, C9.1, J5.1, J6.1, R3.1, U1.16 (3V3), U2.1 (VCC), U5.1 (VCC)
5V: C1.1, C2.1, C3.1, C4.1, J1.1, J2.1, J4.1, U3.7 (VDD)
/LED_PWR: J4.2, Q1.3 (D)
GND: C1.2, C2.2, C3.2, C4.2, C5.2, C6.2, C8.2, C9.2, J1.4, J2.4, J5.3, J6.4, Q1.2 (S), R2.1, R5.2, U1.1 (GND), U1.22 (GND), U1.33 (GND), U2.2 (GND), U3.6 (GND), U5.2 (GND)
unnamed: J1.2, J2.2
unnamed: J1.3, J2.3
unnamed: J5.2, U1.18 (IO_13/TCK)
unnamed: J6.2, U1.27 (IO_21/SDA_1), U2.3 (SDA)
unnamed: J6.3, U1.25 (IO_22/SCL_1), U2.4 (SCL)
unnamed: U1.31 (IO_16/U2_RX), U5.3 (SCL/SPC)
unnamed: U1.32 (IO_04), U5.4 (SDA/SDI/SDO)
unnamed: R3.2, U5.6 (CS)
unnamed: U1.30 (IO_12/TDI), U5.7 (INT1)
unnamed: Q1.1 (G), R4.2, R5.1
unnamed: U1.14 (IO_05/SS), U3.1 (LRCLK)
unnamed: R4.1, U1.29 (IO_17/U2_TXC)
unnamed: U1.8 (IO_18/CLK), U3.5 (~SD_MODE)
unnamed: U1.10 (IO_19/MISO), U3.3 (DIN)
unnamed: U1.12 (IO_23/MOSI), U3.2 (BCLK)
unnamed: R2.2, U3.4 (GAIN_SLOT)

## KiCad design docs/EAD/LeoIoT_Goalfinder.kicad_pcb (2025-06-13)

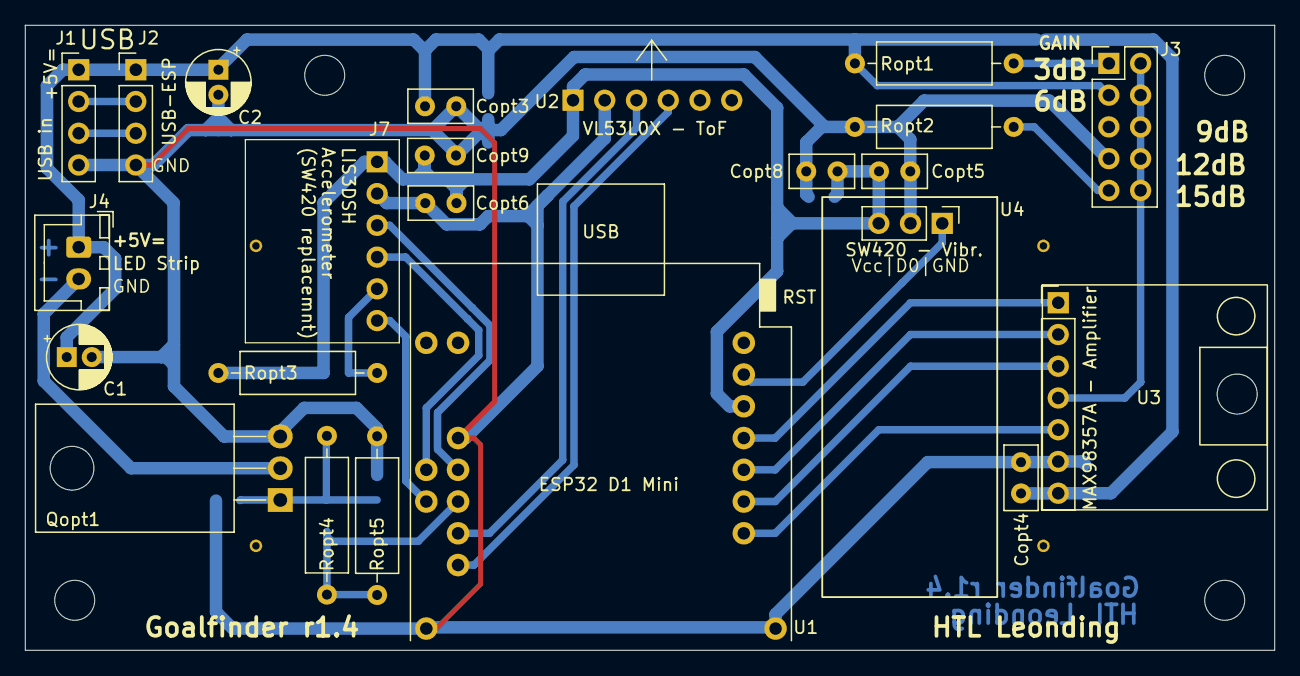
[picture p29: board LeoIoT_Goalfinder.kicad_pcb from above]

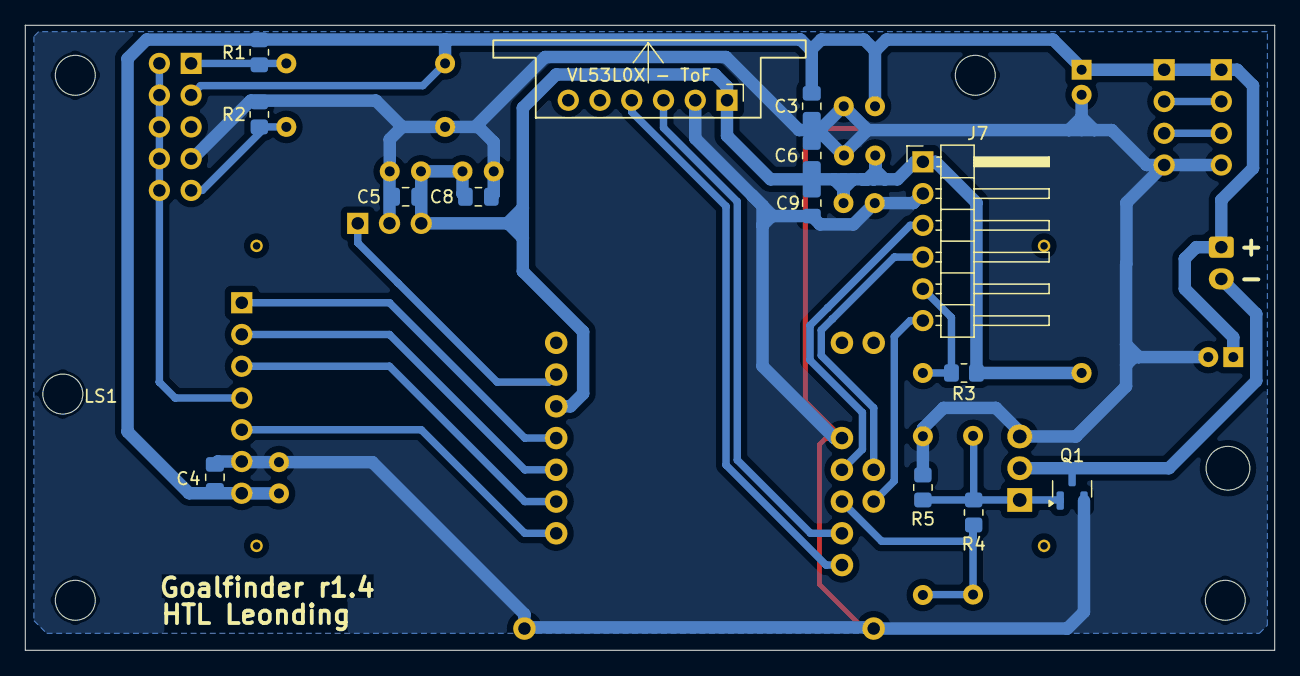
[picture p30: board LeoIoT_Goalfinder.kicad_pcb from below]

Board: 2 copper layers, 100.0 x 50.0 mm, 41 parts (15 on the bottom side), 22 nets.

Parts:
C1: 22µF; CP_Radial_D5.0mm_P2.00mm
C2: 4,7µF; CP_Radial_D5.0mm_P2.00mm
C3, C4, C5, C6, C8, C9: 100nF; C_0805_2012Metric_Pad1.18x1.45mm_HandSolder
Copt3, Copt4, Copt5, Copt6, Copt8, Copt9: 100nF; C_Disc_D5.0mm_W2.5mm_P2.50mm
J1: USB in; PinHeader_1x04_P2.54mm_Vertical
J2: USB-ESP; PinHeader_1x04_P2.54mm_Vertical
J3: GAIN; PinHeader_2x05_P2.54mm_Vertical
J4: LED Strip; JST_XH_B2B-XH-A_1x02_P2.54mm_Vertical
J7: LIS3DH; PinHeader_1x06_P2.54mm_Horizontal
LS1: Speaker; Mono-Enclosed_Speaker_70x30x17mm_onboard
MH1, MH2, MH3, MH3#2, MH4: MountingHole_3.2mm_M3
Q1: IRLML2502; SOT-23
Qopt1: IRLML2502; TO-220-3_Horizontal_TabDown
R1, R2, R3: 100k; R_0805_2012Metric_Pad1.20x1.40mm_HandSolder
R4: 1k; R_0805_2012Metric_Pad1.20x1.40mm_HandSolder
R5: 33k; R_0805_2012Metric_Pad1.20x1.40mm_HandSolder
Ropt1, Ropt2, Ropt3: 100k; R_Axial_DIN0309_L9.0mm_D3.2mm_P12.70mm_Horizontal
Ropt4: 1k; R_Axial_DIN0309_L9.0mm_D3.2mm_P12.70mm_Horizontal
Ropt5: 33k; R_Axial_DIN0309_L9.0mm_D3.2mm_P12.70mm_Horizontal
U1: ESP32 D1 Mini; ESP32_D1_mini
U2: VL53L0X - ToF; VL53L0X_Breakout_Board_vertical_flat
U3: MAX98357A - Amplifier; MAX98357A_Breakout_Board
U4: SW240 - Vcc/D0/GND; SW420_Breakout_Board_Horizontal

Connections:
3V3: C5.1, C6.1, C8.1, C9.1, Copt5.1, Copt6.1, Copt8.1, Copt9.1, J7.1, R3.1, Ropt3.1, U1.16 (3V3), U2.1 (VCC), U4.3
5V: C1.1, C2.1, C3.1, C4.1, Copt3.1, Copt4.1, J1.1, J2.1, J3.3, J4.1, R1.1, Ropt1.1, U3.7 (VDD)
/LED_PWR: J4.2, Q1.3 (D), Qopt1.2 (S)
GND: C1.2, C2.2, C3.2, C4.2, C5.2, C6.2, C8.2, C9.2, Copt3.2, Copt4.2, Copt5.2, Copt6.2, Copt8.2, Copt9.2, J1.4, J2.4, J3.7, J7.2, Q1.2 (S), Qopt1.3 (D), R2.1, R5.2, Ropt2.1, Ropt5.2, U1.1 (GND), U1.22 (GND), U1.33 (GND), U2.2 (GND), U3.6 (GND), U4.2
unnamed: J1.2, J2.2
unnamed: J1.3, J2.3
unnamed: J3.1, R1.2, Ropt1.2
unnamed: J3.9, R2.2, Ropt2.2
unnamed: U1.18 (IO_13/TCK), U4.1
unnamed: U1.27 (IO_21/SDA_1), U2.3 (SDA)
unnamed: U1.25 (IO_22/SCL_1), U2.4 (SCL)
unnamed: J7.3, U1.31 (IO_16/U2_RX)
unnamed: J7.4, U1.32 (IO_04)
unnamed: J7.5, R3.2, Ropt3.2
unnamed: J7.6, U1.30 (IO_12/TDI)
unnamed: Q1.1 (G), Qopt1.1 (G), R4.2, R5.1, Ropt4.2
unnamed: U1.14 (IO_05/SS), U3.1 (LRCLK)
unnamed: R4.1, Ropt4.1, Ropt5.1, U1.29 (IO_17/U2_TXC)
unnamed: U1.8 (IO_18/CLK), U3.5 (~SD_MODE)
unnamed: U1.10 (IO_19/MISO), U3.3 (DIN)
unnamed: U1.12 (IO_23/MOSI), U3.2 (BCLK)
unnamed: J3.2, J3.4, J3.6, J3.8, J3.10, U3.4 (GAIN_SLOT)

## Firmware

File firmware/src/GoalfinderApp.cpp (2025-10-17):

#include <GoalfinderApp.h>
// #include <Arduino.h>
#include <HardwareSerial.h>
#include <Settings.h>
#include <HTTPClient.h>
#include <ArduinoJson.h>
#include <ESPmDNS.h>

#define WEBAPP_DOMAIN "goalfinder"

// Cleanup - replaced by constants
// #define RANGE_WHEN_BALL_GOES_IN 180
// #define VIBRATION_WHEN_BALL_HITS_BOARD 2000

const int GoalfinderApp::wifiTimeout = 10; // In Seconds
const int GoalfinderApp::pinTofSda = 22;
const int GoalfinderApp::pinTofScl = 21;
const int GoalfinderApp::pinI2sBclk = 23;
const int GoalfinderApp::pinI2sWclk = 5;
const int GoalfinderApp::pinI2sDataOut = 19;
const int GoalfinderApp::pinLedPwm = 17;
const int GoalfinderApp::pinRandomSeed = 36;

const int GoalfinderApp::ledPwmChannel = 0;

// const int GoalfinderApp::ballHitDetectionDistance = 180; // TODO: Make configurable
const int GoalfinderApp::shotVibrationThreshold = 3000; // TODO: Make configurable??
const int GoalfinderApp::maxShotDurationMs = 1500;//3500;      // TODO: Mtake configurable

//const char *GoalfinderApp::waitingClip = "/waiting.mp3";

const char *GoalfinderApp::hitClips[] = {
    "/hit-1.mp3",
    // "/hit-2.mp3",
};

const int GoalfinderApp::hitClipsCnt = sizeof(GoalfinderApp::hitClips) / sizeof(GoalfinderApp::hitClips[0]);

const char *GoalfinderApp::tickClips[] = {
    "/tick-1.mp3",
    "/waiting.mp3",
    "/tick-4.mp3"
};

const int GoalfinderApp::tickClipsCnt = sizeof(GoalfinderApp::tickClips) / sizeof(GoalfinderApp::tickClips[0]);

const char *GoalfinderApp::missClips[] = {
    "/miss-1.mp3",
    "/miss-3.mp3",
    "/miss-2.mp3",
};
const int GoalfinderApp::missClipsCnt = sizeof(GoalfinderApp::missClips) / sizeof(GoalfinderApp::missClips[0]);

GoalfinderApp::GoalfinderApp() : Singleton<GoalfinderApp>(),
                                 fileSystem(true),
                                 webServer(&fileSystem),
                                 sntp(),
                                 audioPlayer(&fileSystem, pinI2sBclk, pinI2sWclk, pinI2sDataOut),
                                 tofSensor(),
                                 vibrationSensor(),
                                 ledController(pinLedPwm, ledPwmChannel),
                                 announcing(false),
                                 metronomeIntervalMs(2000),
                                 lastMetronomeTickTime(0),
                                 announcement(Announcement::None),
                                 lastShockTime(0)
{
}

void GoalfinderApp::SetIsSoundEnabled(bool value)
{
    this->isSoundEnabled = value;
}

bool GoalfinderApp::IsSoundEnabled()
{
    return this->isSoundEnabled;
}

bool GoalfinderApp::GetIsClient()
{
    return this->isClient;
}

int GoalfinderApp::GetDetectedHits()
{
    return detectedHits;
}

int GoalfinderApp::GetDetectedMisses()
{
    return detectedMisses;
}

GoalfinderApp::~GoalfinderApp()
{
    MDNS.end();
    webServer.Stop();
}

void GoalfinderApp::InitAP()
{
    if (!MDNS.begin(WEBAPP_DOMAIN))
    {
        Serial.println("[ERROR] Could not start mDNS service!");
    }

    Settings *settings = Settings::GetInstance();

    String ssid = settings->GetDeviceName();
    String wifiPw = settings->GetDevicePassword();

    WiFi.mode(WIFI_AP);
    WiFi.softAP(ssid, wifiPw);
    WiFi.setSleep(false);
    Serial.println(WiFi.softAPIP());
}

void GoalfinderApp::Init()
{
    delay(100); // swing in ;)
    Serial.begin(115200);
    randomSeed(analogRead(pinRandomSeed));

    // TODO: Replace all serial outputs with "Log" for a more fine grained logging control
    if (!fileSystem.Begin())
    {
        Serial.println("FS initialization failed");
        return;
    }
    else
    {
        Serial.println("FS initialized");
    }

    Settings *settings = Settings::GetInstance();

    WiFi.mode(WIFI_STA);
    WiFi.begin("GoalFinder Hub");

    int timeout = 0;

    while (WiFi.status() != WL_CONNECTED && timeout <= wifiTimeout)
    {
        delay(1000);
        timeout += 1;
        Serial.print(".");
    }

    if (timeout <= wifiTimeout)
    {
        Serial.println(WiFi.localIP());

        HTTPClient http;
        http.begin("http://goalfinderhub.local:3000/api/devices/");

        JsonDocument doc;

        doc["macAddress"] = settings->GetMacAddress();
        doc["ipAddress"] = WiFi.localIP().toString();
        doc["deviceName"] = settings->GetDeviceName();
        doc["devicePassword"] = settings->GetDevicePassword();
        doc["vibrationSensorSensitivity"] = settings->GetVibrationSensorSensitivity();
        doc["volume"] = settings->GetVolume();
        doc["ledMode"] = (int)settings->GetLedMode();

        String requestBody;
        serializeJson(doc, requestBody);

        http.addHeader("Content-Type", "application/json");
        int responseCode = http.POST(requestBody);

        if (responseCode == 204)
        {
            Serial.printf("HTTP POST success: %d\n", responseCode);
            String response = http.getString();
            Serial.println(response);

            this->isClient = true;
        }
        else
        {
            Serial.printf("HTTP POST failed: %s\n", http.errorToString(responseCode).c_str());
        }

        http.end();
    }

    if (!this->isClient)
    {
        SetIsSoundEnabled(true);
        InitAP();
    }

    webServer.Begin();

    sntp.Init();
    vibrationSensor.Init();
    tofSensor.Init(pinTofScl, pinTofSda);

    ledController.SetMode(LedMode::Flash);

    UpdateSettings(true);
}

void GoalfinderApp::Process()
{
    // Serial.printf("%4.3f: processing ...\n", millis() / 1000.0);
    UpdateSettings();

    if (this->isSoundEnabled)
    {
        audioPlayer.Loop();
        DetectShot();
        ProcessAnnouncement();
        ledController.Loop();

        if (!audioPlayer.IsPlaying())
        {
            TickMetronome();
        }
    }

    delay(1); // For webserver
}

void GoalfinderApp::UpdateSettings(bool force)
{
    Settings *settings = Settings::GetInstance();
    if (force || settings->IsModified())
    {
        audioPlayer.SetVolume(settings->GetVolume());
        ledController.SetMode(settings->GetLedMode());
        vibrationSensor.SetSensitivity(settings->GetVibrationSensorSensitivity());
        // TODO: Add metronome interval in milliseconds
        // TODO: Add "expert mode" for LED:
        // TODO: Add LED fade in time (softness),
        // TODO: Add LED on time (shine),
        // TODO: Add LED fade out time (softness),
        // TODO: Add option to sync LED fade out time with fade in time,
        // TODO: Add LED off time (dark),
        // TODO: Add number of repetitions (see "Turbo"),
        // TODO: Add blank time (only when for more than 1 repetition - see Turbo),
        // TODO: Implement a generic LED controller method based on the settings above
        //       and reimplement predefined LED controller patterns to set those settings accordingly
    }
}

void GoalfinderApp::ResetDetectedHits()
{
    detectedHits = 0;
}

void GoalfinderApp::ResetDetectedMisses()
{
    detectedMisses = 0;
}

void GoalfinderApp::TickMetronome()
{
    unsigned long currentTime = millis();
    if ((currentTime - lastMetronomeTickTime) > metronomeIntervalMs)
    {
        lastMetronomeTickTime = currentTime;
        //const char *clipName = tickClips[0];
        const char *clipName = tickClips[Settings::GetInstance()->GetMetronomeSound()];
        /*if (lastShockTime > 0)
        {
            // shot detection pending
            clipName = waitingClip;
        }*/
        PlaySound(clipName);
    }
}

void GoalfinderApp::OnShotDetected()
{
    announcement = Announcement::Shot;
    Serial.printf("%4.3f: announce shot: %d\n", millis() / 1000.0, announcement);
}

void GoalfinderApp::AnnounceHit()
{
    announcement = Announcement::Hit;
    detectedHits++;

    if (this->isClient)
    {
        HTTPClient http;
        http.begin("http://goalfinderhub.local:3000/api/games/hit");
        http.addHeader("Content-Type", "application/json");

        JsonDocument doc;

        doc["macAddress"] = Settings::GetInstance()->GetMacAddress();

        String requestBody;
        serializeJson(doc, requestBody);

        int responseCode = http.POST(requestBody);

        if (responseCode != 204)
        {
            Serial.printf("HTTP POST on hit failed: %s\n", http.errorToString(responseCode).c_str());
        }
    }
    // Serial.printf("%4.3f: announce hit: %d\n", millis() / 1000.0, announcement);
}

void GoalfinderApp::AnnounceMiss()
{
    announcement = Announcement::Miss;
    detectedMisses++;
    // Serial.printf("%4.3f: announce miss: %d\n", millis() / 1000.0, announcement);
}

void GoalfinderApp::ProcessAnnouncement()
{
    // Serial.printf("%4.3f: processing announcements: %d\n", millis() / 1000.0, announcement);
    switch (announcement)
    {
    case Announcement::Shot:
        AnnounceEvent("-> shot", 0);
        // Send websocket
        break;
    case Announcement::Hit:
        //AnnounceEvent("-> hit", hitClips[0]);
        AnnounceEvent("-> hit", hitClips[Settings::GetInstance()->GetHitSound()]);
        break;
    case Announcement::Miss:
        //AnnounceEvent("-> miss", missClips[0]);
        AnnounceEvent("-> miss", missClips[Settings::GetInstance()->GetMissSound()]);
        break;
    default:
        break;
    }
    announcement = Announcement::None;
}

void GoalfinderApp::AnnounceEvent(const char *traceMsg, const char *sound)
{
    Serial.printf("%4.3f: announcing event '%s'\n", millis() / 1000.0, traceMsg);
    if (sound != 0)
    {
        announcing = true;
        PlaySound(sound);
    }
}

void GoalfinderApp::PlaySound(const char *soundFileName)
{
    if (soundFileName != 0)
    {
        Serial.printf("%4.3f: starting playback of: '%s'\n", millis() / 1000.0, soundFileName != 0 ? soundFileName : "NULL");
        audioPlayer.PlayMP3(soundFileName);
    }
}
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

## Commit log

2024-03-05 Changed framework to arduino
2024-03-12 Added pin configuration
    [Pin_Configuration.fzz]
2024-03-12 Added image of pin configuration
    [Pin_Configuration.fzz]
2024-03-14 Updated pin configuration
    [Pin_Configuration.fzz]
2024-04-04 Made library for tof sensor
2024-04-25 added output to tof sensor
2024-05-26 updated schematic added PCB views
2024-05-26 added KiCAD sources
    [LeoIoT_Goalfinder.kicad_pcb, LeoIoT_Goalfinder.kicad_sch]
2024-05-27 updated PCB layout (extended wire width)
    [LeoIoT_Goalfinder.kicad_pcb]
2024-05-28 finished PCB introduced housing
    [LeoIoT_Goalfinder.kicad_pcb]
2024-05-28 Added some translations to web app
    [LeoIoT_Goalfinder.kicad_pcb, LeoIoT_Goalfinder.kicad_sch]
2024-05-28 added power support capacities, updated schematic and PCB to r1.1
    [LeoIoT_Goalfinder.kicad_pcb, LeoIoT_Goalfinder.kicad_sch]
2024-05-31 improved HW: - added capacitors for each breakout board - made GND lines wider and added GND shield areas - added HW revision 01.02 added technical drawings for case factoring
    [LeoIoT-Goalfinder-Case-r01.00_Bottom.dxf, LeoIoT-Goalfinder-Case-r01.00_Top.dxf, LeoIoT-Goalfinder-Case-r01.00_Wall-front_and_back.dxf, LeoIoT-Goalfinder-Case-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]
2024-06-03 updated PCB r 01.02
    [LeoIoT_Goalfinder.kicad_pcb]
2024-06-04 made led fade
2024-06-18 added led
2024-06-19 Fixed LED Controller
2024-06-19 added 4 LED-Modus, LED Vue
2024-06-19 made LED Controller compilable fixed constants in App AppGoalfinder: moved constants and instances into class scope replaced sound clips added sound clip fond added 3D models for mounting poles
    [Distance-16.4.stl, Distance-19.stl]
2024-06-19 added SwuOTA page sample
2024-06-19 integrated LedController fixed LedController
2024-06-19 added c-tor ledChannel
2024-06-19 finished LedController
2024-06-19 implemented ledmode in settings
2024-06-19 added off button in LED Modes
2024-06-19 updated mounting poles
    [Distance-16.4.stl, Distance-19.stl]
2024-07-01 updated distance pole models
    [Distance-16.4.stl, Distance-19.stl]
2024-12-11 Refined design and PCB layout and added BOM - added SMD resistors - shaped PCB prints
    [LeoIoT_Goalfinder.kicad_pcb, LeoIoT_Goalfinder.kicad_sch, LeoIoT_Goalfinder_BOM.xlsx]
2025-01-08 #1 Added power button in webapp
2025-01-29 updated BOM
    [LeoIoT_Goalfinder_BOM.xlsx]
2025-05-03 added schematic and PCBs for r1.3
2025-06-13 added r1.4 of PCB and SMD-only PCB layout as well as production files
    [LeoIoT_Goalfinder-B_Cu.gbr, LeoIoT_Goalfinder-B_Mask.gbr, LeoIoT_Goalfinder-B_Paste.gbr, LeoIoT_Goalfinder-B_Silkscreen.gbr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]
2025-06-13 finalized Goalfinder r1.4 + added optional accelerometer + added solder pads / pins for external USB socket and USB plug to ESP32 + added 'compact' variant with only SMD components + created producti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
    [LeoIoT_Goalfinder-B_Cu.gbr, LeoIoT_Goalfinder-B_Mask.gbr, LeoIoT_Goalfinder-B_Paste.gbr, LeoIoT_Goalfinder-B_Silkscreen.gbr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]
2025-06-16 update Goalfinder Case with back-mount options
2025-06-19 Added printable model for powerbank holder for Anker 10Ah powerbanks
    [Powerbank-Holder_Anker.stl]
2025-08-11 updated schematics
    [LeoIoT_Goalfinder.kicad_sch]
2025-09-14 frontend for lidar sensor detection distance
2025-09-17 updated goalfinder case zu rev 1.1
    [JST-SYP_Female.step, JST-SYP_Male.step, LeoIoT-Goalfinder-Case-r01.00_Bottom.dxf, LeoIoT-Goalfinder-Case-r01.00_Top.dxf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]
2025-10-17 added case plates with openings (and logo)
